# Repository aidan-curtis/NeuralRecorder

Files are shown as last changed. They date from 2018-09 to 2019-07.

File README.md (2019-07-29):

<iframe style="width: 100%" height = "500" src="https://www.youtube.com/embed/SluLUA3ErF0" frameborder="0" allow="accelerometer; autoplay; encrypted-media; gyroscope; picture-in-picture" allowfullscreen></iframe>

## Problem Statement
According to the World Health Organization, up to 50 million people in the world have epilepsy. Of these 50 million, 30% do not respond to medication to keep their seizures under control. These patients are said to have intractable epilepsy, and one of the most effective ways of treating these patients is to record patient EEG data in order to determine the source of the seizures, and then remove the specific part of the brain that is causing the seizures. This process of recording data is invasive and requires implanting electrodes into the brain. These electrodes are wired from inside the brain to a stationary external source that collects the data. The presence of wires causes two main problems: 1) the patients have limited mobility throughout the duration of the data recording and must remain in the hospital for days or even weeks, and 2) the wires are a potential source of infection.

Remaining in the hospital for an extended period of time is extremely expensive, and if the wires were to cause an infection, that cost would only go up. The estimated cost for this procedure is about $10,000 a day. Additionally, being unable to move about unrestricted is detrimental to the patient’s general well-being.

We aim to design a device that can be implanted into a patient’s brain and transmit EEG data wirelessly. Such a device can decrease hospital stay with the possibility of the patient going home for the duration of the recording process, and will drastically decrease the cost of the process. Additionally, even if the patient must remain in the hospital, our device will allow the patient to move about the room freely, which will greatly improve their quality of life. Lastly, our device will also implement novel data compression techniques prior to transmission, which sets our product apart from existing solutions.

## Project Scope
We will build a fully functioning wireless neural recording system that uses data compression to efficiently transmit local field potentials and/or single unit action potential data from patients to a nearby data collection device.

It will contain four major subsystems:
- A power management system
- Frontend interface chip that does signal conditioning
- A wireless link to a receiver
- A novel data compression implementation

With a budget of $2,500 and working between August 29, 2018 and April 11, 2019 we must meet or exceed a minimum set of requirements:
- 48 electrode channels consisting of 6 probes with 8 electrodes each
- A battery life 24 hours or greater
- An ADC resolution of at least 8 bits
- Ability to wirelessly transmit data at least 1 meter
- A Sampling rate of at least 1000 Hz

## Final Design

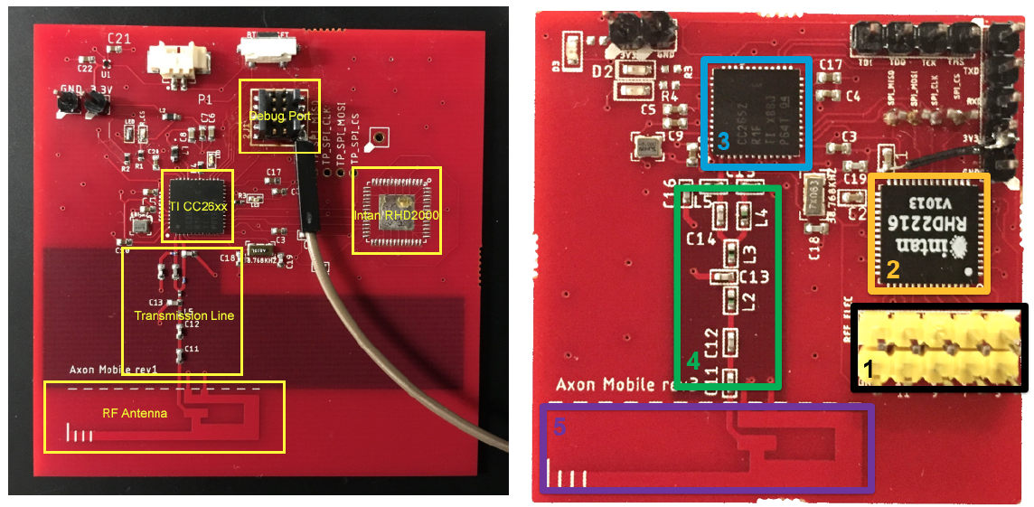
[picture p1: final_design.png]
Final Design


## Intracranial Testing
<iframe style="width: 100%" height = "500" src="https://www.youtube.com/embed/LJeJShj3aGc" frameborder="0" allow="accelerometer; autoplay; encrypted-media; gyroscope; picture-in-picture" allowfullscreen></iframe>

## ISCAS World Champions
We placed first in the ISCAS Compatition in Sapporo, Japan.
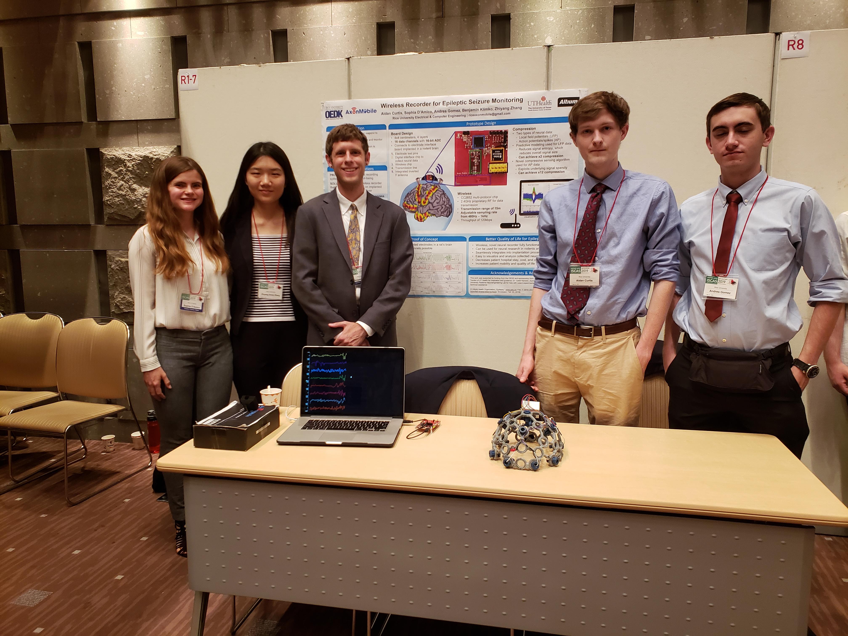
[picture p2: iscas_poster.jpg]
ISCAS Award

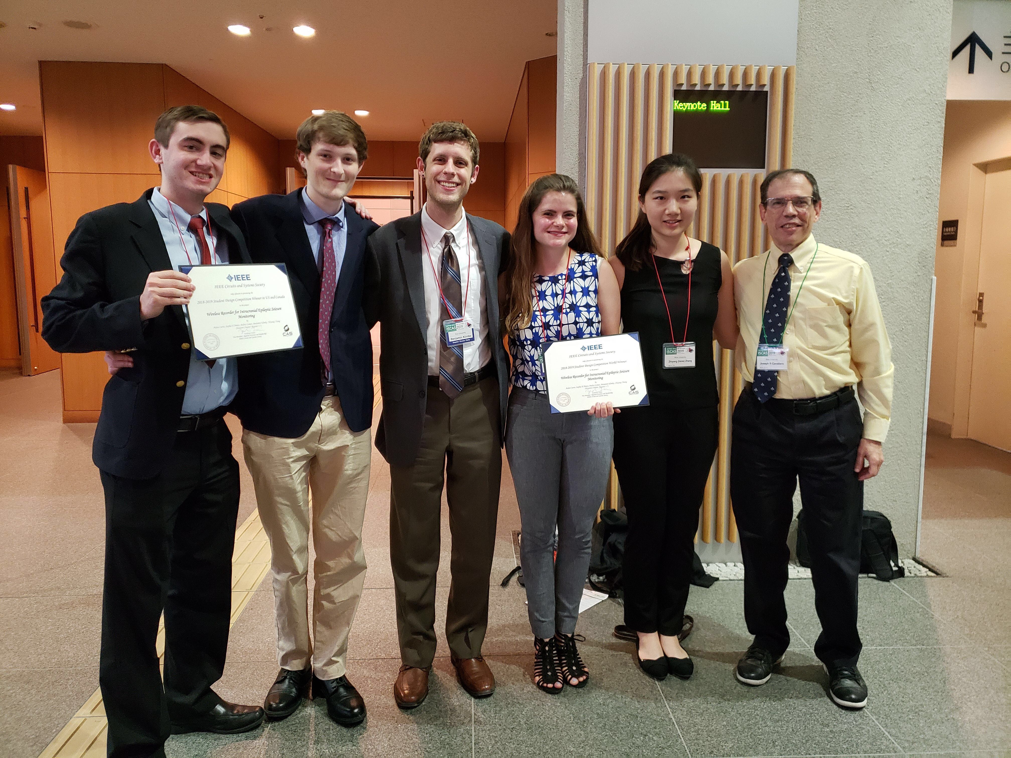
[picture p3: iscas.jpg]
ISCAS Poster


## Full Report
[Download Full Report PDF]( FullReport.pdf )

## Team
Team Axon Mobile
- *Aidan Curtis:* arc11 at rice dot edu
- *Sophie D'Amico:* srd5 at rice dot edu
- *Benjamin Klimko:* bhk2 at rice dot edu
- *Irene Zhang:* zz36 at rice dot edu
- *Andres Gomez:* aeg6 at rice dot edu

## Sponsorship
Thanks to Altium for sponsoring our team and providing us with Altium Designer so we can easily and efficiently create custom PCBs for our project.

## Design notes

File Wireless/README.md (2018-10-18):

### Stream Data From An Arduino
Code to be updated. You need to install Matlab Arduino support first 
https://www.mathworks.com/hardware-support/arduino-matlab.html

### Writing code for TI MCUs
* You can use TI CCS Cloud IDE for development. Go to https://dev.ti.com/ and select CCS Cloud.
* Import Project Empty, run the code and follow instructions to install Chrome 
extension and cloud dependencies. 

### View Throughput
* SmartRF Protocol Packet Sniffer http://www.ti.com/tool/packet-sniffer can be used to 
see the data that are being broadcasted

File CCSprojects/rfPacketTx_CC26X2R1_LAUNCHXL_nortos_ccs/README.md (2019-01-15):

---
# rfpackettx

---

Example Summary
---------------
The Packet TX example illustrates how to do simple packet transmission using
the RF driver. This example is meant to be used with the Packet RX
example or SmartRF Studio. For every packet transmitted, Board_PIN_LED1 is
toggled.  The frequency and other RF settings can be modified using SmartRF
Studio.

Peripherals Exercised
---------------------
* `Board_PIN_LED1` - Toggled when data is transmitted over the RF interface

Resources & Jumper Settings
---------------------------
> If you're using an IDE (such as CCS or IAR), please refer to Board.html in
your project directory for resources used and board-specific jumper settings.
Otherwise, you can find Board.html in the directory
&lt;SDK_INSTALL_DIR&gt;/source/ti/boards/&lt;BOARD&gt;.

Example Usage
-------------
Run the example. On another board, run the Packet RX example.
Board_PIN_LED1 is toggled when data is transmitted.

Application Design Details
--------------------------
This examples consists of a single task and the exported SmartRF Studio radio
settings.

The default frequency is 868.0 MHz. In order to change frequency, modify the
smartrf_settings file. This can be done using the code export feature in
Smart RF Studio, or directly in the file.

The default frequency is 868.0 MHz, in order to change RF settings please
modify the smartrf_settings.c file.
This can be done either by exporting from Smart RF Studio or directly in the
file.

When the task is executed it:

1. Configures the radio for Proprietary mode
2. Gets access to the radio via the RF drivers RF_open
3. Sets up the radio using CMD_PROP_RADIO_DIV_SETUP command
4. Set the output power to 14 dBm (requires that CCFG_FORCE_VDDR_HH = 1 in
ccfg.c)
5. Sets the frequency using CMD_FS command
6. Create packet (with increasing sequence number and random content)
7. Set absolute TX time to utilize automatic power management
8. Transmit packet using CMD_PROP_TX command with blocking RF driver call
9. Toggle Board_PIN_LED1 to indicate packet transmitted
10. Transmit packets forever by repeating step 6-9

Note for IAR users: When using the CC1310DK, the TI XDS110v3 USB Emulator must
be selected. For the CC1310_LAUNCHXL, select TI XDS110 Emulator. In both cases,
select the cJTAG interface.

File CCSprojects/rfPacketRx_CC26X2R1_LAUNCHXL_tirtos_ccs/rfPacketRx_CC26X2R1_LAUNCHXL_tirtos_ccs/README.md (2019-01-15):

---
# rfpacketrx

---

Example Summary
---------------
The Packet RX example illustrates how to do simple packet RX using the
RF driver. This example is meant to be used with the Packet TX example or
SmartRF Studio. For every packet received, Board_PIN_LED2 is toggled.
The frequency and other RF settings can be modified using SmartRF Studio.

Peripherals Exercised
---------------------
* `Board_PIN_LED2` - Toggled when data is received over the RF interface

Resources & Jumper Settings
---------------------------
> If you're using an IDE (such as CCS or IAR), please refer to Board.html in
your project directory for resources used and board-specific jumper settings.
Otherwise, you can find Board.html in the directory
&lt;SDK_INSTALL_DIR&gt;/source/ti/boards/&lt;BOARD&gt;.

Example Usage
-------------
Run the example. On another board, run the EasyLink TX example.
Board_PIN_LED2 is toggled when data with CRC OK is received.

Application Design Details
--------------------------
This examples consists of a single task and the exported SmartRF Studio radio
settings.

The default frequency is 868.0 MHz. In order to change frequency, modify the
smartrf_settings file. This can be done using the code export feature in
Smart RF Studio, or directly in the file.

The default frequency is 868.0 MHz, in order to change RF settings please
modify the smartrf_settings.c file.
This can be done either by exporting from Smart RF Studio or directly in the
file.

When the task is executed it:

1. Configures the radio for Proprietary mode
2. Gets access to the radio via the RF drivers RF_open
3. Sets up the radio using CMD_PROP_RADIO_DIV_SETUP command
4. Defines a data queue to handle received data
5. Sets the frequency using CMD_FS command
6. Sends the CMD_PROP_RX command to start receiving data
7. Once data with CRC OK is received we toggle the
   Board_PIN_LED2 and re-enter RX with the CMD_PROP_RX command

Note for IAR users: When using the CC1310DK, the TI XDS110v3 USB Emulator must
be selected. For the CC1310_LAUNCHXL, select TI XDS110 Emulator. In both cases,
select the cJTAG interface.

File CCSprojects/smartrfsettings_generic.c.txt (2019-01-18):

//*********************************************************************************
// These settings have been generated for use with TI-RTOS and cc26xxware
//
// Generated by SmartRF Studio version 2.3.0
// Tested with TI-RTOS version tirtos_simplelink_2_16_xx_xx
//
//*********************************************************************************

//*********************************************************************************
// Parameter summary
// Address: aa-bb
// Frequency: 2445.00000 MHz
// Data Format: Serial mode disable
// Deviation: 50.000 kHz
// Packet Length Config: Variable
// Max Packet Length: 128
// Packet Length: 30
// RX Filter BW: 220 kHz
// Symbol Rate: 50.00000 kBaud
// Sync Word Length: 32 Bits
// TX Power: 5 dBm
// Whitening: No whitening

#include <ti/devices/DeviceFamily.h>
#include DeviceFamily_constructPath(driverlib/rf_mailbox.h)
#include DeviceFamily_constructPath(driverlib/rf_common_cmd.h)
#include DeviceFamily_constructPath(driverlib/rf_prop_cmd.h)

#include <ti/drivers/rf/RF.h>
#include "smartrf_settings.h"

// TI-RTOS RF Mode Object
RF_Mode RF_prop =
{
    .rfMode = RF_MODE_PROPRIETARY_2_4,
//    .rfMode = RF_MODE_BLE,
    .cpePatchFxn = 0, //&rf_patch_cpe_genfsk,
    .mcePatchFxn = 0, //&rf_patch_mce_genfsk,
    .rfePatchFxn = 0, //&rf_patch_rfe_genfsk,
};

uint32_t shape[] = {0x00000000, 0x00000000, 0x00000000, 0x360c0100, 0xacaba076, 0xacacacac};

// Overrides for CMD_PROP_RADIO_SETUP
uint32_t pOverrides[] = {
 // override_agama_48_mhz_crystal.xml
 // Calculate the frequencies for synth based on 48MHz crystal (default is 24MHz).
 (uint32_t)0x00400403,
 // override_turn_off_dcdc_option.xml
 // Set DCDCCTL5[3:0]=0x0, Turn off optimization of DCDC regulator in TX
 (uint32_t)0x000088D3,
 // Set DCDCCTL5[3:0]=0x0, Turn off optimization of DCDC regulator in RX
 (uint32_t)0x000088C3,
 (uint32_t)0xFFFFFFFF,
};

// CMD_PROP_RADIO_SETUP
rfc_CMD_PROP_RADIO_SETUP_t RF_cmdPropRadioDivSetup =
{
    .commandNo = 0x3806,
    .status = 0x0000,
    .pNextOp = 0, // INSERT APPLICABLE POINTER: (uint8_t*)&xxx
    .startTime = 0x00000000,
    .startTrigger.triggerType = 0x0,
    .startTrigger.bEnaCmd = 0x0,
    .startTrigger.triggerNo = 0x0,
    .startTrigger.pastTrig = 0x0,
    .condition.rule = 0x1,
    .condition.nSkip = 0x0,
    .modulation.modType = 0x1,
    .modulation.deviation = 200,
    .symbolRate.preScale = 15,
    .symbolRate.rateWord = 131072,
    .rxBw = 7,
    .preamConf.nPreamBytes = 0x8,
    .preamConf.preamMode = 0x0,
    .formatConf.nSwBits = 16,
    .formatConf.bBitReversal = 0x0,
    .formatConf.bMsbFirst = 0x1,
    .formatConf.fecMode = 0x0,
    .formatConf.whitenMode = 0x0,
    .config.frontEndMode = 0x0,
    .config.biasMode = 0x0,
    .config.analogCfgMode = 0x0,
    .config.bNoFsPowerUp = 0x0,
    .txPower = 0x9324,
    .pRegOverride = pOverrides,
};

// CMD_FS
rfc_CMD_FS_t RF_cmdFs =
{
    .commandNo = 0x0803,
    .status = 0x0000,
    .pNextOp = 0, // INSERT APPLICABLE POINTER: (uint8_t*)&xxx
    .startTime = 0x00000000,
    .startTrigger.triggerType = 0x0,
    .startTrigger.bEnaCmd = 0x0,
    .startTrigger.triggerNo = 0x0,
    .startTrigger.pastTrig = 0x0,
    .condition.rule = 0x1,
    .condition.nSkip = 0x0,
    .frequency = 2440,
    .fractFreq = 0x0000,
    .synthConf.bTxMode = 1,
    .synthConf.refFreq = 0x0,
};

// CMD_PROP_TX
rfc_CMD_PROP_TX_t RF_cmdPropTx =
{
    .commandNo = 0x3801,
    .status = 0x0000,
    .pNextOp = 0, // INSERT APPLICABLE POINTER: (uint8_t*)&xxx
    .startTime = 0x00000000,
    .startTrigger.triggerType = 0x0,
    .startTrigger.bEnaCmd = 0x0,
    .startTrigger.triggerNo = 0x0,
    .startTrigger.pastTrig = 0x0,
    .condition.rule = 0x1,
    .condition.nSkip = 0x0,
    .pktConf.bFsOff = 0x0,
    .pktConf.bUseCrc = 0x1,
    .pktConf.bVarLen = 0x1,
    .pktLen = 0x7d, // SET APPLICATION PAYLOAD LENGTH
    .syncWord = 0xD391D391,
    .pPkt = 0, // INSERT APPLICABLE POINTER: (uint8_t*)&xxx
};

// CMD_PROP_RX
rfc_CMD_PROP_RX_t RF_cmdPropRx =
{
    .commandNo = 0x3802,
    .status = 0x0000,
    .pNextOp = 0, // INSERT APPLICABLE POINTER: (uint8_t*)&xxx
    .startTime = 0x00000000,
    .startTrigger.triggerType = 0x0,
    .startTrigger.bEnaCmd = 0x0,
    .startTrigger.triggerNo = 0x0,
    .startTrigger.pastTrig = 0x0,
    .condition.rule = 0x1,
    .condition.nSkip = 0x0,
    .pktConf.bFsOff = 0x0,
    .pktConf.bRepeatOk = 0x0,
    .pktConf.bRepeatNok = 0x0,
    .pktConf.bUseCrc = 0x1,
    .pktConf.bVarLen = 0x1,
    .pktConf.bChkAddress = 0x0,
    .pktConf.endType = 0x0,
    .pktConf.filterOp = 0x0,
    .rxConf.bAutoFlushIgnored = 0x0,
    .rxConf.bAutoFlushCrcErr = 0x0,
    .rxConf.bIncludeHdr = 0x1,
    .rxConf.bIncludeCrc = 0x0,
    .rxConf.bAppendRssi = 0x0,
    .rxConf.bAppendTimestamp = 0x0,
    .rxConf.bAppendStatus = 0x1,
    .syncWord = 0xD391D391,
    .maxPktLen = 0x7d, // MAKE SURE DATA ENTRY IS LARGE ENOUGH
//    .pktConf.addressMode = 0, // CHANGE!
    .address0 = 0xaa,
    .address1 = 0xbb,
    .endTrigger.triggerType = 0x1,
    .endTrigger.bEnaCmd = 0x0,
    .endTrigger.triggerNo = 0x0,
    .endTrigger.pastTrig = 0x0,
    .endTime = 0x00000000,
    .pQueue = 0, // INSERT APPLICABLE POINTER: (dataQueue_t*)&xxx
    .pOutput = 0, // INSERT APPLICABLE POINTER: (uint8_t*)&xxx
};

// CMD_TX_TEST
rfc_CMD_TX_TEST_t RF_cmdTxTest =
{
        .commandNo = 0x0808,
        .status = 0x0000,
        .pNextOp = 0, /*INSERT APPLICABLE POINTER: (uint8_t*)&xxx */
        .startTime = 0x00000000,
        .startTrigger.triggerType = 0x0,
        .startTrigger.bEnaCmd = 0x0,
        .startTrigger.triggerNo = 0x0,
        .startTrigger.pastTrig = 0x0,
        .condition.rule = 0x1,
        .condition.nSkip = 0x0,
        .config.bUseCw = 0x0,
        .config.bFsOff = 0x0,
        .config.whitenMode = 0x2,
        .__dummy0 = 0x00,
        .txWord = 0xabcd,
        .__dummy1 = 0x00,
        .endTrigger.triggerType = 0x1,
        .endTrigger.bEnaCmd = 0x0,
        .endTrigger.triggerNo = 0x0,
        .endTrigger.pastTrig = 0x0,
        .syncWord = 0x930b51de,
        .endTime = 0x00000000,
};

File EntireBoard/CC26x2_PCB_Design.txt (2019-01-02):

CC26x2 Doc List
=======================
General
CC26xx Tools Overview
	- http://processors.wiki.ti.com/index.php/CC13xx_CC26xx_Tools_Overview#Using_CCS_v6.1_with_XDS110_and_CC13xx.2FCC26xx
CC2652R1 Quick Start Guide
	- http://www.ti.com/lit/ml/swru528/swru528.pdf
CC26x0 SimpleLink Wireless MCU Technical Reference Guide
	- http://www.ti.com/lit/ug/swcu185a/swcu185a.pdf
Production Test and Programming for CC26xx
	- http://processors.wiki.ti.com/index.php/Production_Test_and_Programming_of_SimpleLink_CC26xx_or_CC13xx_Wireless_MCUs
Design a product with CC26xx
	- http://processors.wiki.ti.com/index.php/Designing_a_Product_with_SimpleLink_CC26xx_or_CC13xx_Wireless_MCUs#Step_6_-_Test_the_hardware
	- Very useful links
-----------------------
PCB Design
CC26xx Hardware Layout Considerations
	- http://processors.wiki.ti.com/images/8/8b/CC26xx_HW_training_Layout_Considerations.pdf
CC26xx RF Frontends and Antennas
	- http://processors.wiki.ti.com/images/4/45/CC26xx_HW_training_RF_Frontends_and_Antennas.pdf
	- Differential vs Single-ended design. Differential vs Balun. External vs Internal bias
2.4GHz Inverted F Antenna
	- http://www.ti.com/lit/an/swru120c/swru120c.pdf
	- GND plane placement wrt antenna
PCB Design Considerations 
	- http://www.ti.com/lit/an/swra640/swra640.pdf 
Johnson Balun for CC26xx Family
	- http://www.ti.com/lit/an/swra572/swra572.pdf 
	- 9 discrete LC components into a single components(basically replacing LC on RF_N and RF_P pins)
	- Complex impedance matching
Hardware Migration from CC26x0 to CC26x2
	- http://www.ti.com/lit/an/swra582/swra582.pdf
Crystal Selection
	- http://processors.wiki.ti.com/index.php/CC26xx_Crystals
XDS110 Debug Probe guide
	- http://www.ti.com/lit/ug/sprui94/sprui94.pdf	
CC Debugger User Guide 
	- http://www.ti.com/lit/ug/swru197h/swru197h.pdf
-----------------------
Software
CC26xx Family SW Quick Start Guide
	- http://processors.wiki.ti.com/index.php/CC26xx_Family_SW_Quickstart_Guide
Flash Programming via JTAG Port
	- https://e2e.ti.com/support/wireless-connectivity/bluetooth/f/538/p/556076/2033879?tisearch=e2e-sitesearch&keymatch=%20user%3A290509#2033879
CC26xx JTAG Flash Programming
	- https://e2e.ti.com/support/wireless-connectivity/bluetooth/f/538/t/521220
SmartRF Flash Programmer User Manual
	- http://www.ti.com/lit/ug/swru069g/swru069g.pdf
	- NOTE that CC26x2 is not supported
CCS Uniflash
	- http://processors.wiki.ti.com/index.php/Category:CCS_UniFlash
Uniflash v4 Quick Guide
	- http://processors.wiki.ti.com/index.php/UniFlash_v4_Quick_Guide
JTAG and Uniflash Video Tutorial
	- https://training.ti.com/using-jtag-ucd3138-introduction-uniflash

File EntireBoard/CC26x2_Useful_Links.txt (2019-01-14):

CC26x2 Doc List
=======================
General
CC2652R Datasheet
	- http://www.ti.com/lit/ds/symlink/cc2652r.pdf
CC26xx Tools Overview
	- http://processors.wiki.ti.com/index.php/CC13xx_CC26xx_Tools_Overview#Using_CCS_v6.1_with_XDS110_and_CC13xx.2FCC26xx
CC2652R1 Quick Start Guide
	- http://www.ti.com/lit/ml/swru528/swru528.pdf
CC26x0 SimpleLink Wireless MCU Technical Reference Guide
	- http://www.ti.com/lit/ug/swcu185a/swcu185a.pdf
Production Test and Programming for CC26xx
	- http://processors.wiki.ti.com/index.php/Production_Test_and_Programming_of_SimpleLink_CC26xx_or_CC13xx_Wireless_MCUs
Design a product with CC26xx
	- http://processors.wiki.ti.com/index.php/Designing_a_Product_with_SimpleLink_CC26xx_or_CC13xx_Wireless_MCUs#Step_6_-_Test_the_hardware
	- Very useful links
-----------------------
PCB Design
CC26xx Hardware Design Checklist
	- http://processors.wiki.ti.com/index.php/CC26xx_HW_Checklist
CC26xx Hardware Layout Considerations
	- http://processors.wiki.ti.com/images/8/8b/CC26xx_HW_training_Layout_Considerations.pdf
CC26xx RF Frontends and Antennas
	- http://processors.wiki.ti.com/images/4/45/CC26xx_HW_training_RF_Frontends_and_Antennas.pdf
	- Differential vs Single-ended design. Differential vs Balun. External vs Internal bias
2.4GHz Inverted F Antenna
	- http://www.ti.com/lit/an/swru120c/swru120c.pdf
	- GND plane placement wrt antenna
CC26xx PCB Design Considerations 
	- http://www.ti.com/lit/an/swra640/swra640.pdf 
Johanson Balun for CC26xx Family
	- http://www.ti.com/lit/an/swra572/swra572.pdf 
	- 9 discrete LC components into a single components(basically replacing LC on RF_N and RF_P pins)
	- Complex impedance matching
Hardware Migration from CC26x0 to CC26x2
	- http://www.ti.com/lit/an/swra582/swra582.pdf
Crystal Selection
	- http://processors.wiki.ti.com/index.php/CC26xx_Crystals
XDS110 Debug Probe guide
	- http://www.ti.com/lit/ug/sprui94/sprui94.pdf	
CC Debugger User Guide 
	- http://www.ti.com/lit/ug/swru197h/swru197h.pdf
-----------------------
Software
CC26xx Family SW Quick Start Guide
	- http://processors.wiki.ti.com/index.php/CC26xx_Family_SW_Quickstart_Guide
Flash Programming via JTAG Port
	- https://e2e.ti.com/support/wireless-connectivity/bluetooth/f/538/p/556076/2033879?tisearch=e2e-sitesearch&keymatch=%20user%3A290509#2033879
CC26xx JTAG Flash Programming
	- https://e2e.ti.com/support/wireless-connectivity/bluetooth/f/538/t/521220
SmartRF Flash Programmer User Manual
	- http://www.ti.com/lit/ug/swru069g/swru069g.pdf
	- NOTE that CC26x2 is not supported
CCS Uniflash
	- http://processors.wiki.ti.com/index.php/Category:CCS_UniFlash
Uniflash v4 Quick Guide
	- http://processors.wiki.ti.com/index.php/UniFlash_v4_Quick_Guide
JTAG and Uniflash Video Tutorial
	- https://training.ti.com/using-jtag-ucd3138-introduction-uniflash

-----------------------
Bluetooth
TI Serial Port Service
	- http://www.ti.com/lit/ug/tidua63/tidua63.pdf

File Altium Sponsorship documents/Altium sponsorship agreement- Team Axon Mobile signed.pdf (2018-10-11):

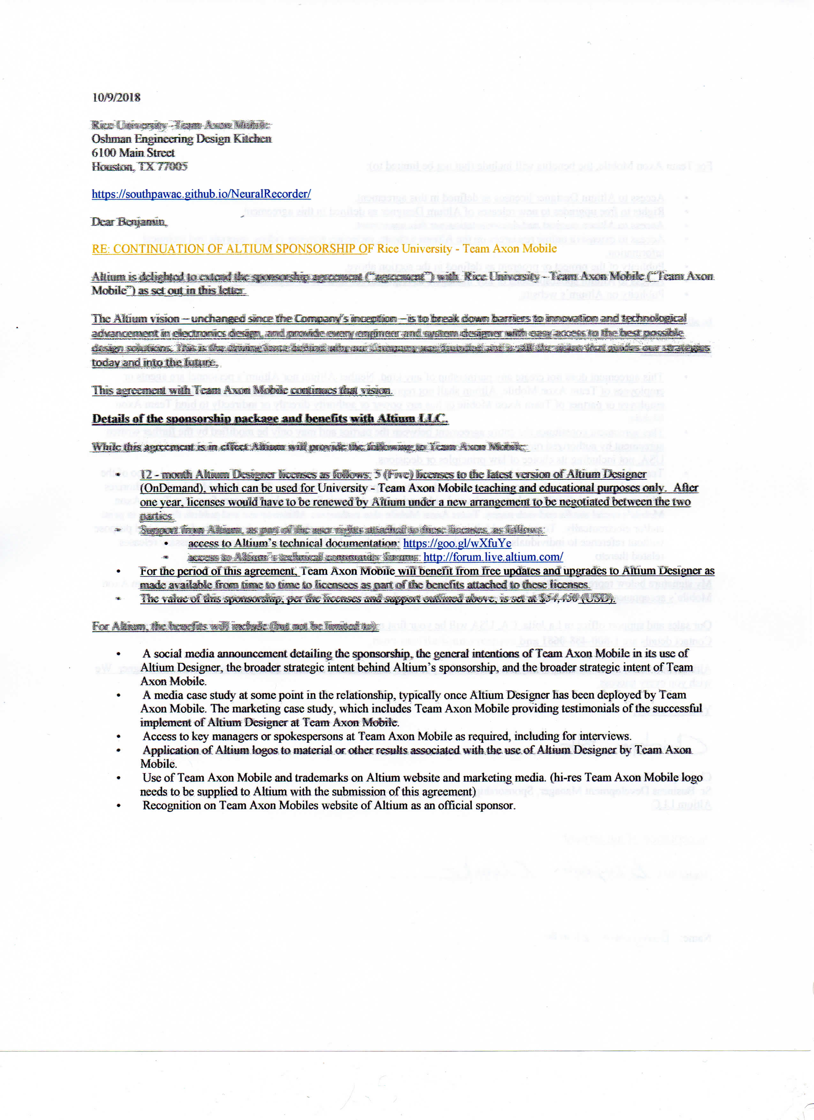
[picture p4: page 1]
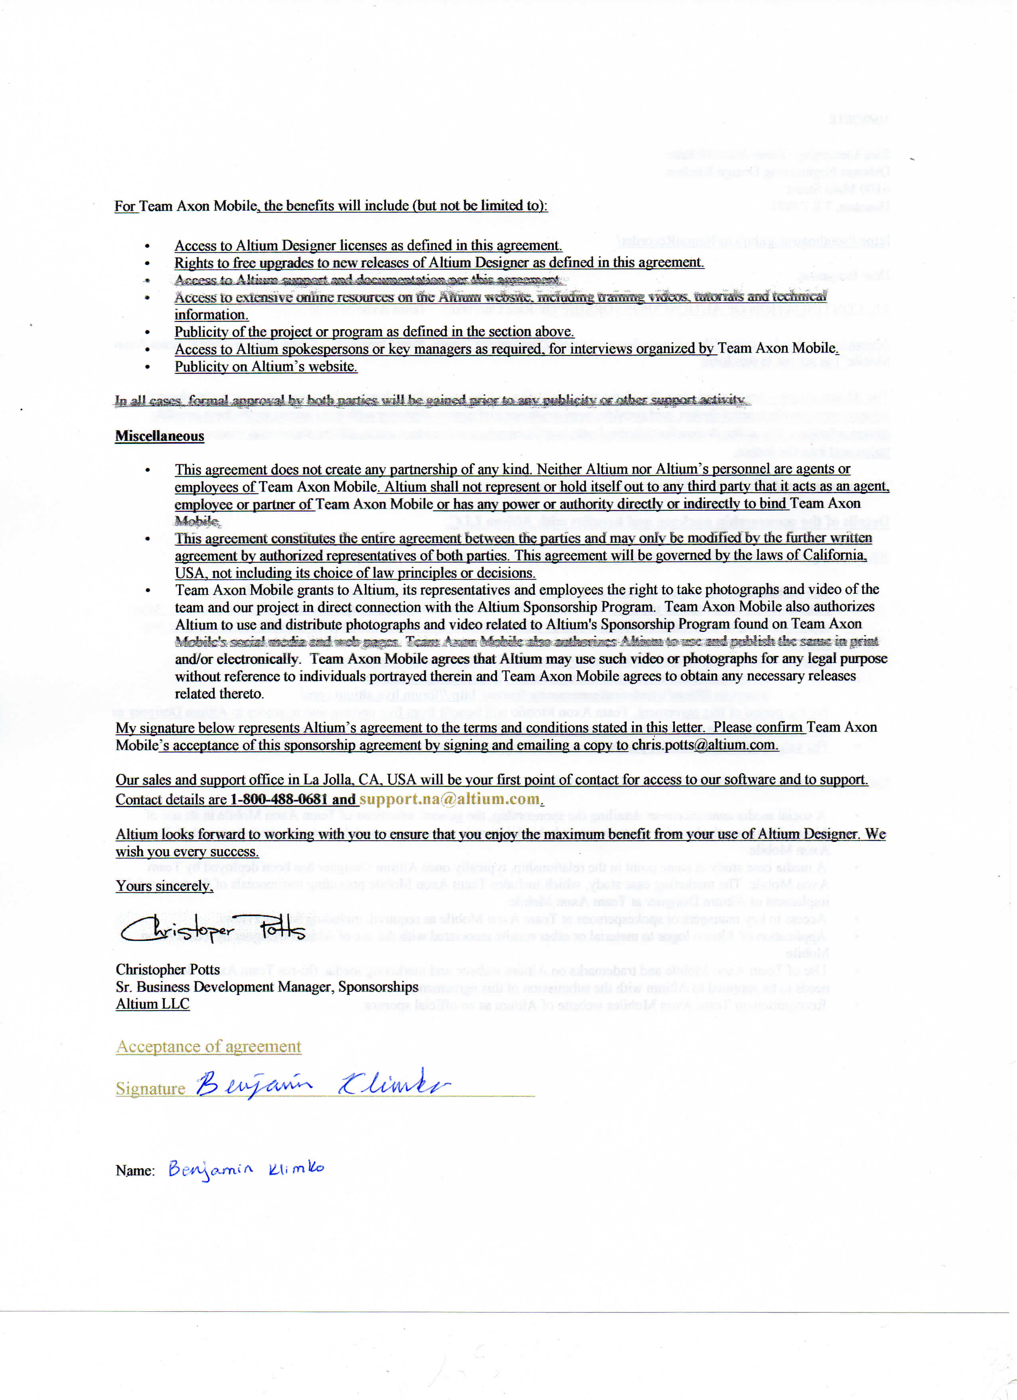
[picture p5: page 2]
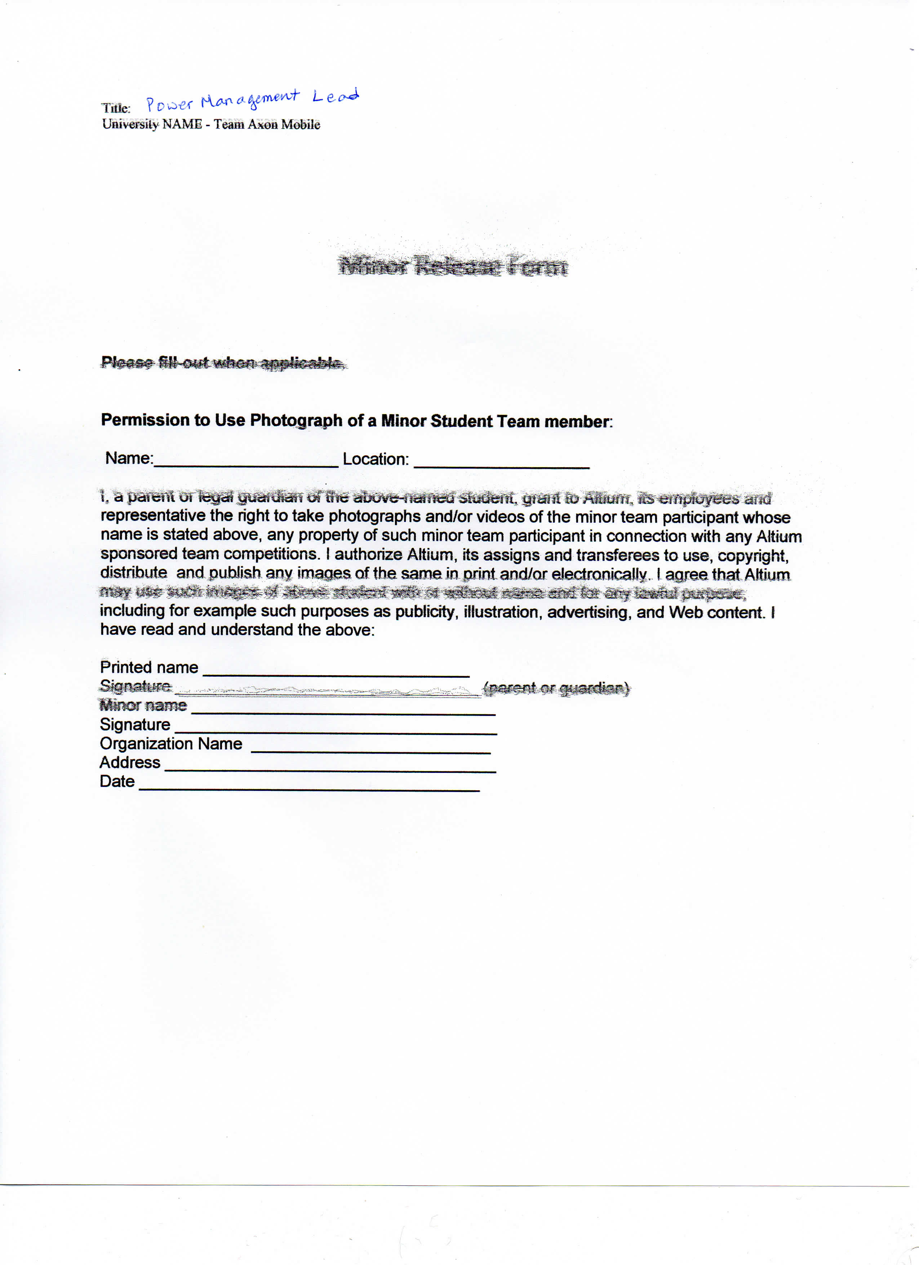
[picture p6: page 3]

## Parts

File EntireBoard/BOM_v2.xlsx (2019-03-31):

Name | Description | MPN | Supplier Name | Supplier Part # | Unit Price | Quantity | Total Price | Link | Datasheet
48MHz Crystal | required as frequency reference for radio | NDK NX2016SA 48.000MHz EXS00A-CS05517 | Digikey | 644-1377-1-ND | $0.86 | 3 | $2.58 | https://www.digikey.com/product-detail/en/ndk-america-inc/NX2016SA-48MHZ-EXS00A-CS05517/644-1377-1-ND/9172105 | https://media.digikey.com/pdf/Data%20Sheets/NDK%20PDFs/NX2016SA-48M-EXS00A-CS05517_Spec.pdf
32.768kH Crystal | reduce power consumption for BLE compared to internal RC oscillator | Epson FC-135 | Digikey | SE2413CT-ND | 0.41 | 3 | $1.23 | https://www.digikey.com/product-detail/en/epson/FC-135-32.7680KA-A3/SE2413CT-ND/569857 | https://support.epson.biz/td/api/doc_check.php?dl=brief_FC-135&lang=en
10pin microheader | connection to XDS110 debugger | FTSH-105-01-F-DV-K-TR | Digikey | SAM13160CT-ND | 3.36 | 3 | $10.08 | https://www.digikey.com/product-detail/en/samtec-inc/FTSH-105-01-F-DV-K-TR/SAM13160CT-ND/8827915 | http://suddendocs.samtec.com/catalog_english/ftsh_smt.pdf
IDC ribbon cable | connection btw XDS110 and CC | Samtek FFSD-05-D-02.00-01-N | Digikey | SAM8217-ND | 7.86 | 1 | $7.86 | https://www.digikey.com/product-detail/en/samtec-inc/FFSD-05-D-02.00-01-N/SAM8217-ND/1106576 | http://suddendocs.samtec.com/catalog_english/ffsd.pdf
current sense resistor | measure power consumption | Panasonic ERJ-MFBAF10MX | Mouser | 667-ERJ-MFBAF10MX | $0.61 | 4 | $2.44 | https://www.mouser.com/ProductDetail/Panasonic/ERJ-MFBAF10MX | https://www.mouser.com/datasheet/2/315/RDN0000C328-1365505.pdf
green led | signal line indication | Bivar SM0402GC | Mouser | 749-SM0402GC | $0.57 | 12 | $6.84 | https://www.mouser.com/ProductDetail/Bivar/SM0402GC | https://www.mouser.com/datasheet/2/50/Bivar-3-22-2017-SM0402GC-1158932.pdf
switch | for resetting mcu | 1188E-1K2-V-T/R | Mouser | 113-1188E1K2VTR | $0.69 | 3 | $2.07 | https://www.mouser.com/ProductDetail/Diptronics/1188E-1K2-V-T-R?qs=MLItCLRbWswadUUxegNFmg%3D%3D | http://www.dip.com.tw/en/en-product-information/en-switch004/item/2445-1188
batteries | powering system | RJD3555HPPV30M | Digikey | 1572-1627-ND | $34.13 | 2 | $68.26 | https://www.digikey.com/product-detail/en/illinois-capacitor/RJD3555HPPV30M/1572-1627-ND/6159145
battery connector | connect the power to the system | 532610271 | Digikey | WM7620CT-ND | $0.98 | 4 | $3.92
1.5 kOhm Ferrite Bead | Part of the power system from cc2650 | BLM18HE152SN1D | Digikey | 490-5216-1-ND | $0.21 | 3 | $0.63 | https://www.digikey.com/product-detail/en/murata-electronics-north-america/BLM18HE152SN1D/490-5216-1-ND/1948392
22uF cap |  | CL05A226MQ5N6J8 | Digikey | 1276-7090-1-ND | $0.58 | 6 | $3.48 | https://www.digikey.com/product-detail/en/samsung-electro-mechanics/CL05A226MQ5N6J8/1276-7090-1-ND/7320732
1.8pF cap |  | 500R07S1R8BV4T | Digikey | 712-1271-1-ND | $0.21 | 3 | $0.63 | https://www.digikey.com/product-detail/en/johanson-technology-inc/500R07S1R8BV4T/712-1271-1-ND/1786733
12pF cap |  | C0402C120J5GACTU | Digikey | 399-1013-1-ND | $0.10 | 12 | $1.20 | https://www.digikey.com/product-detail/en/kemet/C0402C120J5GACTU/399-1013-1-ND/411288
1pF cap |  | 500R07S1R0BV4T | Digikey | 712-1266-1-ND | $0.21 | 9 | $1.89 | https://www.digikey.com/product-detail/en/johanson-technology-inc/500R07S1R0BV4T/712-1266-1-ND/1786728
6.8 uH inductor |  | AIML-0603-6R8K-T | Digikey | 535-11606-1-ND | $0.10 | 3 | $0.30 | https://www.digikey.com/product-detail/en/abracon-llc/AIML-0603-6R8K-T/535-11606-1-ND/2782848
2nH inductor |  | MHQ0603P2N0BTD25 | Mouser | 810-MHQ0603P2N0BTD25 | $0.60 | 6 | $3.60 | https://www.mouser.com/ProductDetail/TDK/MHQ0603P2N0BTD25
2.4nH inductor |  | LQP03TN2N4B02D | Digikey | 490-6724-1-ND | $0.10 | 6 | $0.60 | https://www.digikey.com/product-detail/en/murata-electronics-north-america/LQP03TN2N4B02D/490-6724-1-ND/5802372
 |  |  |  |  |  |  | $117.61

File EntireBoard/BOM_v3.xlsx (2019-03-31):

Name | Description | Manufacturer | MPN | Supplier Name | Supplier Part # | Unit Price | Quantity | Total Price | Link
48MHz Crystal | required as frequency reference for radio | NDK | NX2016SA 48.000MHz EXS00A-CS05517 | Digikey | 644-1377-1-ND | $0.86 | 5 | $4.30 | https://www.digikey.com/product-detail/en/ndk-america-inc/NX2016SA-48MHZ-EXS00A-CS05517/644-1377-1-ND/9172105
32.768kH Crystal | reduce power consumption for BLE compared to internal RC oscillator | Epson | FC-135 | Digikey | SE2413CT-ND | 0.41 | 5 | $2.05 | https://www.digikey.com/product-detail/en/epson/FC-135-32.7680KA-A3/SE2413CT-ND/569857
solderpaste |  | chipquik | SMD291SNL | mouser | 910-SMD291SNL | $15.29 | 0 | $0.00 | https://www.mouser.com/ProductDetail/Chip-Quik/SMD291SNL
10pin microheader | connection to XDS110 debugger | samtek | FTSH-105-01-F-DV-K-TR | Digikey | SAM13160CT-ND | 3.36 | 3 | $10.08 | https://www.digikey.com/product-detail/en/samtec-inc/FTSH-105-01-F-DV-K-TR/SAM13160CT-ND/8827915
IDC ribbon cable | connection btw XDS110 and CC | samtek | FFSD-05-D-02.00-01-N | Digikey | SAM8217-ND | 7.86 | 0 | $0.00 | https://www.digikey.com/product-detail/en/samtec-inc/FFSD-05-D-02.00-01-N/SAM8217-ND/1106576
current sense resistor | measure power consumption | Panasonic | ERJ-MFBAF10MX | Mouser | 667-ERJ-MFBAF10MX | $0.61 | 5 | $3.05 | https://www.mouser.com/ProductDetail/Panasonic/ERJ-MFBAF10MX
red led | indicator light 0603 | osram | LS L296-P2Q2-1 | mouser | 720-LSL296-P2Q2-1-Z | 0.52 | 5 | $2.60 | https://www.mouser.com/ProductDetail/OSRAM-Opto-Semiconductors/LS-L296-P2Q2-1
green led | signal line indication 0603 | osram | LP L296-J2L2-25 | Mouser | 720-LPL296J2L225Z | 0.57 | 5 | $2.85 | https://www.mouser.com/ProductDetail/OSRAM-Opto-Semiconductors/LP-L296-J2L2-25
button | for resetting mcu |  | 1188E-1K2-V-T/R | Mouser | 113-1188E1K2VTR | $0.69 | 0 | $0.00 | https://www.mouser.com/ProductDetail/Diptronics/1188E-1K2-V-T-R?qs=MLItCLRbWswadUUxegNFmg%3D%3D
switch | power on | E-switch | EG1271 | mouser | 612-EG1271 | $0.76 | 5 | $3.80 | https://www.mouser.com/ProductDetail/E-Switch/EG1271
batteries | powering system |  | RJD3555HPPV30M | Digikey | 1572-1627-ND | $34.13 | 0 | $0.00 | https://www.digikey.com/product-detail/en/illinois-capacitor/RJD3555HPPV30M/1572-1627-ND/6159145
battery connector | connect the power to the system |  | 532610271 | Digikey | WM7620CT-ND | $0.98 | 5 | $4.90 | https://www.digikey.com/product-detail/en/molex/0532610271/WM7620CT-ND/699107
1.5 kOhm Ferrite Bead | Part of the power system from cc2650 |  | BLM18HE152SN1D | Digikey | 490-5216-1-ND | $0.21 | 5 | $1.05 | https://www.digikey.com/product-detail/en/murata-electronics-north-america/BLM18HE152SN1D/490-5216-1-ND/1948392
22uF cap | match TI 0603 | murata | GRM188R60J226MEA0D | mouser | 81-GRM188R60J226ME0D | $0.20 | 10 | $1.95 | https://www.mouser.com/ProductDetail/Murata-Electronics/GRM188R60J226MEA0D?qs=sGAEpiMZZMs0AnBnWHyRQE145Nb6Pjkyo3rf03lmerU%3D
1.8pF cap | match TI 0402 | murata | GRM1555C1H1R8CA01D | mouser | 81-GRM1555C1H1R8CA1D | $0.04 | 10 | $0.40 | https://www.mouser.com/ProductDetail/Murata-Electronics/GRM1555C1H1R8CA01D?qs=sGAEpiMZZMs0AnBnWHyRQJFx1SN4r7R8jjRyTSAQsik%3D
12pF cap | match TI 0402 | murata | GRM1555C1H120JA01D | mouser | 81-GRM1555C1H120JA1D | $0.04 | 20 | $0.80 | https://www.mouser.com/ProductDetail/Murata-Electronics/GRM1555C1H120JA01D?qs=sGAEpiMZZMs0AnBnWHyRQJFx1SN4r7R8pM7YbelYqII%3D
1pF cap | match TI 0402 | murata | GRM1555C1H1R0CA01D | mouser | 81-GRM1555C1H1R0CA1D | $0.04 | 15 | $0.66 | https://www.mouser.com/ProductDetail/Murata-Electronics/GRM1555C1H1R0CA01D
0.1uF cap | match TI | murata | GRM155R71E104KE14D | mouser | 81-GRM155R71E104KE4D | $0.10 | 0 | $0.00
6.8 uH inductor | match TI 0805 | tdk | MLZ2012N6R8LT000 | mouser | 810-MLZ2012N6R8LT000 | $0.14 | 5 | $0.70 | https://www.mouser.com/ProductDetail/TDK/MLZ2012N6R8LT000
6.8uH inductor | 603 | TDK | MLF1608E6R8JT000 | mouser | 810-MLF1608E6R8JT000 | $0.14 | 5 | $0.70 | https://www.mouser.com/ProductDetail/TDK/MLF1608E6R8JT000
2nH inductor 0402 | match TI 0402 | murata | LQG15HS2N0S02D | Mouser | 81-LQG15HS2N0S02D | $0.06 | 10 | $0.56 | https://www.mouser.com/ProductDetail/Murata-Electronics/LQG15HS2N0S02D
2.4nH inductor | match TI 0402 | murata | LQG15HS2N4S02D | mouser | 81-LQG15HS2N4S02D | $0.06 | 10 | $0.60 | https://www.mouser.com/ProductDetail/Murata-Electronics/LQG15HS2N4S02D
intan chip!!!
cc2652 |  |  |  |  |  |  |  | $41.05
linear regulator

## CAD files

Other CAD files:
CCSprojects/ble5_project_zero_cc26x2r1lp_app/FlashROM_Debug/Startup/main.obj
CCSprojects/ble5_project_zero_cc26x2r1lp_app/TOOLS/src/sysbios/m3_Hwi_asm.obj
CCSprojects/rfPacketRx_CC26X2R1_LAUNCHXL_tirtos_ccs/tirtos_builds_CC26X2R1_LAUNCHXL_release_ccs/src/sysbios/m3_IntrinsicsSupport_asm.obj
CCSprojects/rfPacketTx_CC26X2R1_LAUNCHXL_tirtos_ccs/tirtos_builds_CC26X2R1_LAUNCHXL_release_ccs/src/sysbios/m3_Hwi_asm.obj
CCSprojects/ble5_project_zero_cc26x2r1lp_app/TOOLS/src/sysbios/m3_IntrinsicsSupport_asm.obj
CCSprojects/rfPacketRx_CC26X2R1_LAUNCHXL_tirtos_ccs/tirtos_builds_CC26X2R1_LAUNCHXL_release_ccs/src/sysbios/m3_Hwi_asm_switch.obj
CCSprojects/rfPacketTx_CC26X2R1_LAUNCHXL_tirtos_ccs/tirtos_builds_CC26X2R1_LAUNCHXL_release_ccs/src/sysbios/m3_TaskSupport_asm.obj
CCSprojects/ble5_project_zero_cc26x2r1lp_app/TOOLS/src/sysbios/m3_Hwi_asm_switch.obj
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

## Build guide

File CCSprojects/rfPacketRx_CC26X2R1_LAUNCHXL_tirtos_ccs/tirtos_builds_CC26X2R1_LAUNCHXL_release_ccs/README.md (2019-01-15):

## Project Summary

This project contains settings to disable the standard debug features in
TI-RTOS.

## Project Usage

This project is intended to be used by applications that need a "production"
TI-RTOS configuration that does not include debug features.  Multiple
applications can use this project.

This project is the default configuration used by most of the SimpleLink
examples. It was selected as the default to minimize code size.

Please refer to the TI-RTOS Kernel section in the SimpleLink MCU SDK User's
Guide for the details on how applications use this project.

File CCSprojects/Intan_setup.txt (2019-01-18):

   //set up the registers
    messages[0] = 0b0000000000000000;
    messages[1] = 0b0000000000000000;
    messages[2] = 0b1000000011011110; //R0
    messages[3] = 0b1000000100100000; //R1
    messages[4] = 0b1000001000101000; //R2
    messages[5] = 0b1000001100000000; //R3
    messages[6] = 0b1000010011001101; //R4
    messages[7] = 0b1000010100000000; //R5
    messages[8] = 0b1000011000000000; //R6
    messages[9] = 0b1000011100000000; //R7
    messages[10] = 0b1000100000001000; //R8
    messages[11] = 0b1000100100000000; //R9
    messages[12] = 0b1000101000000100; //R10
    messages[13] = 0b1000101100000000; //R11
    messages[14] = 0b1000110000010000; //R12
    messages[15] = 0b1000110101111100; //R13
    messages[16] = 0b1000111011111111; //R14
    messages[17] = 0b1000111111111111; //R15
    messages[18] = 0b1001000011111111; //R16
    messages[19] = 0b1001000111111111; //R17
    messages[20] = 0b0000000000000000;
    messages[21] = 0b0000000000000000;
    messages[22] = 0b0000000000000000;
    messages[23] = 0b0000000000000000;
    messages[24] = 0b0101010100000000; // Config
    messages[25] = 0b0000000000000000;
    messages[26] = 0b0000000000000000;
    messages[27] = 0b0000000000000000;
    messages[28] = 0b0000000000000000;
    messages[29] = 0b0000000000000000;
    messages[30] = 0b0000000000000000;
    messages[31] = 0b0000000000000000;
    messages[32] = 0b0000000000000000;
    messages[33] = 0b0000000000000000;
    messages[34] = 0b0000000000000000;
    messages[35] = 0b0000000000000000;
    messages[36] = 0b1110100000000000; //I
    messages[37] = 0b1110100100000000; //N
    messages[38] = 0b1110101000000000; //T
    messages[39] = 0b1110101100000000; //A
    messages[40] = 0b1110110000000000; //N

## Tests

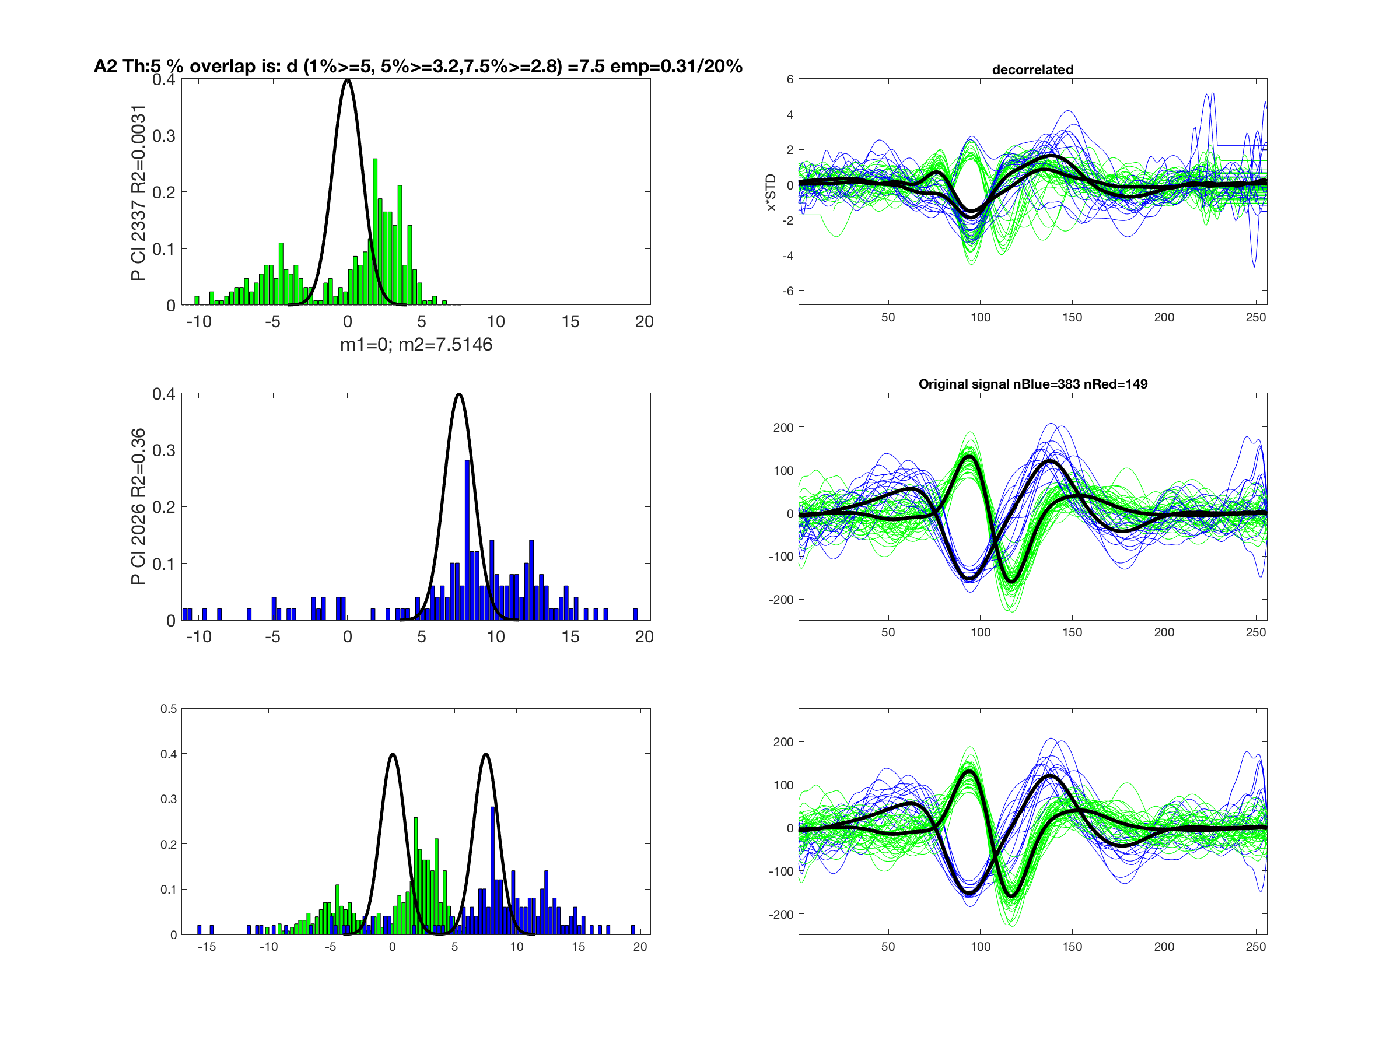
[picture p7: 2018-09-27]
Compression/Mess/5/A2_SepTest_2337_2026_THM_1.png

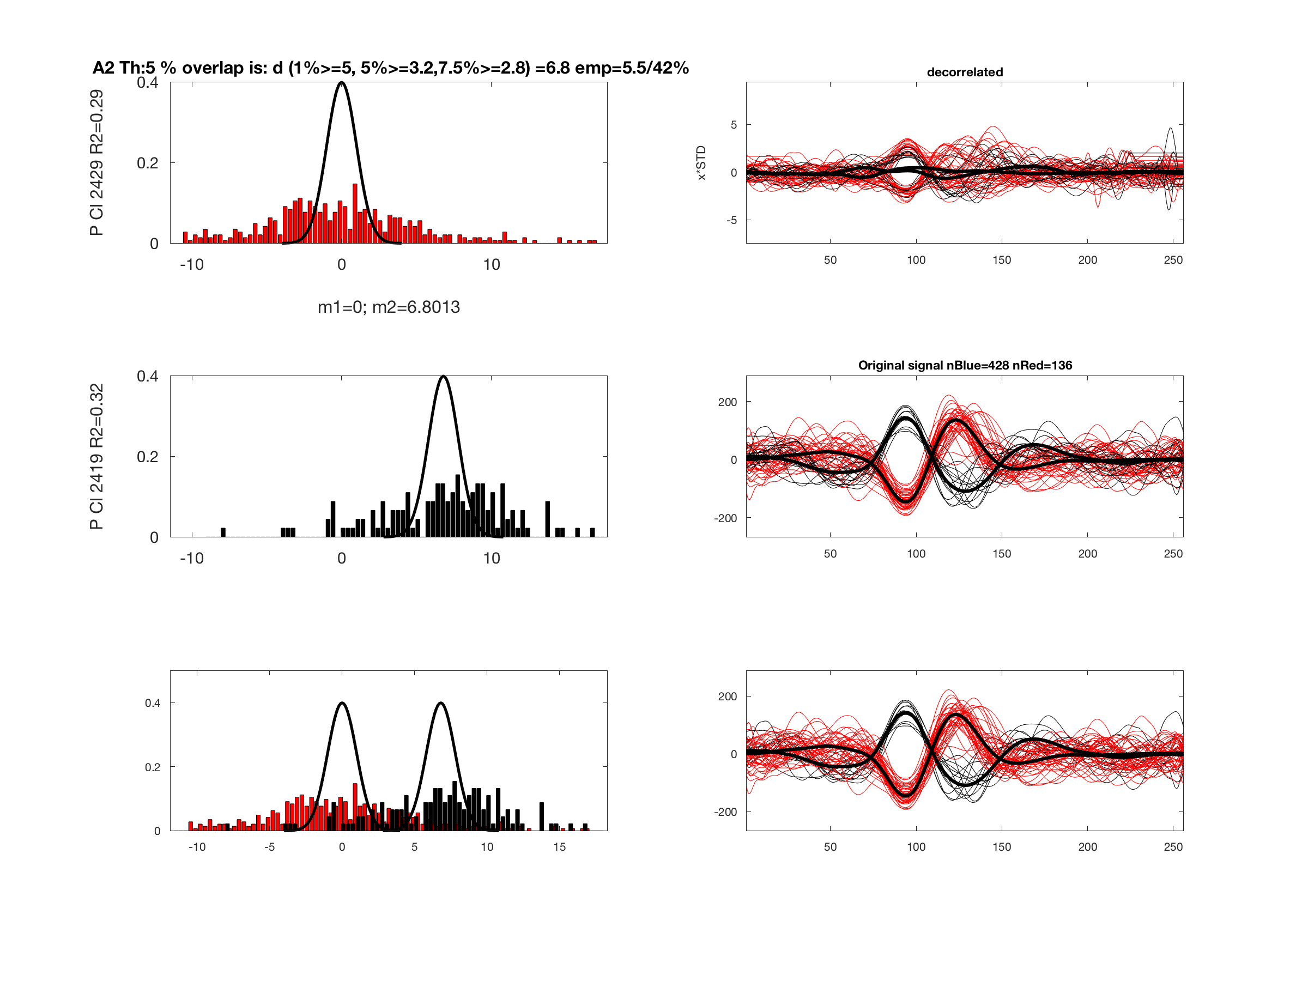
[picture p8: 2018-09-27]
Compression/Mess/5/A2_SepTest_2429_2419_THM_1.png

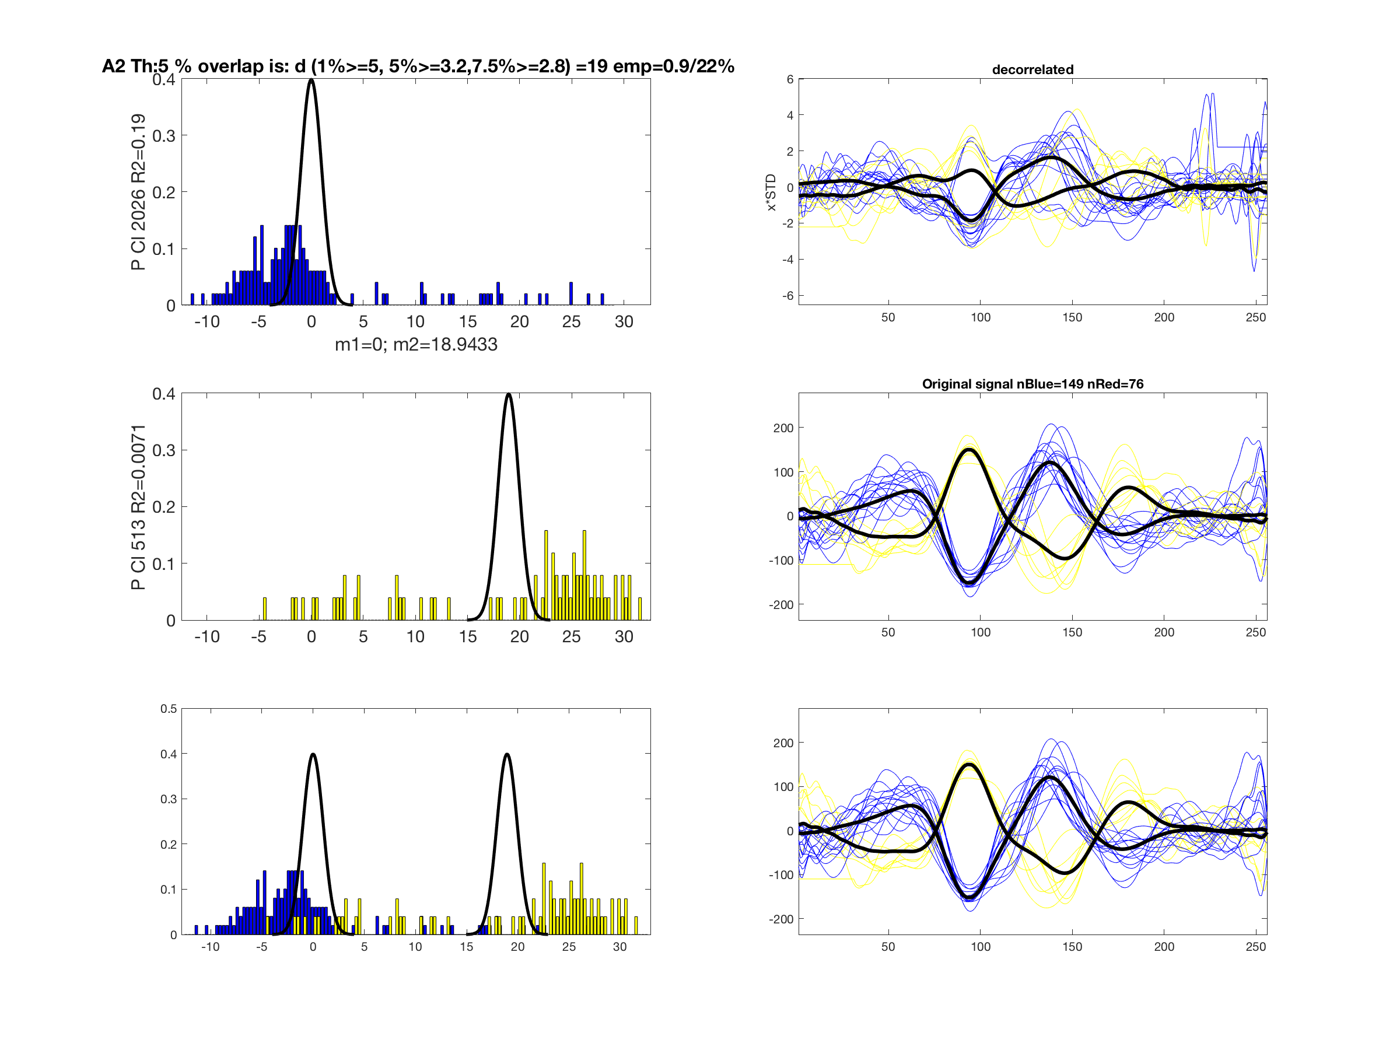
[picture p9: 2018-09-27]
Compression/Mess/5/A2_SepTest_2026_513_THM_1.png

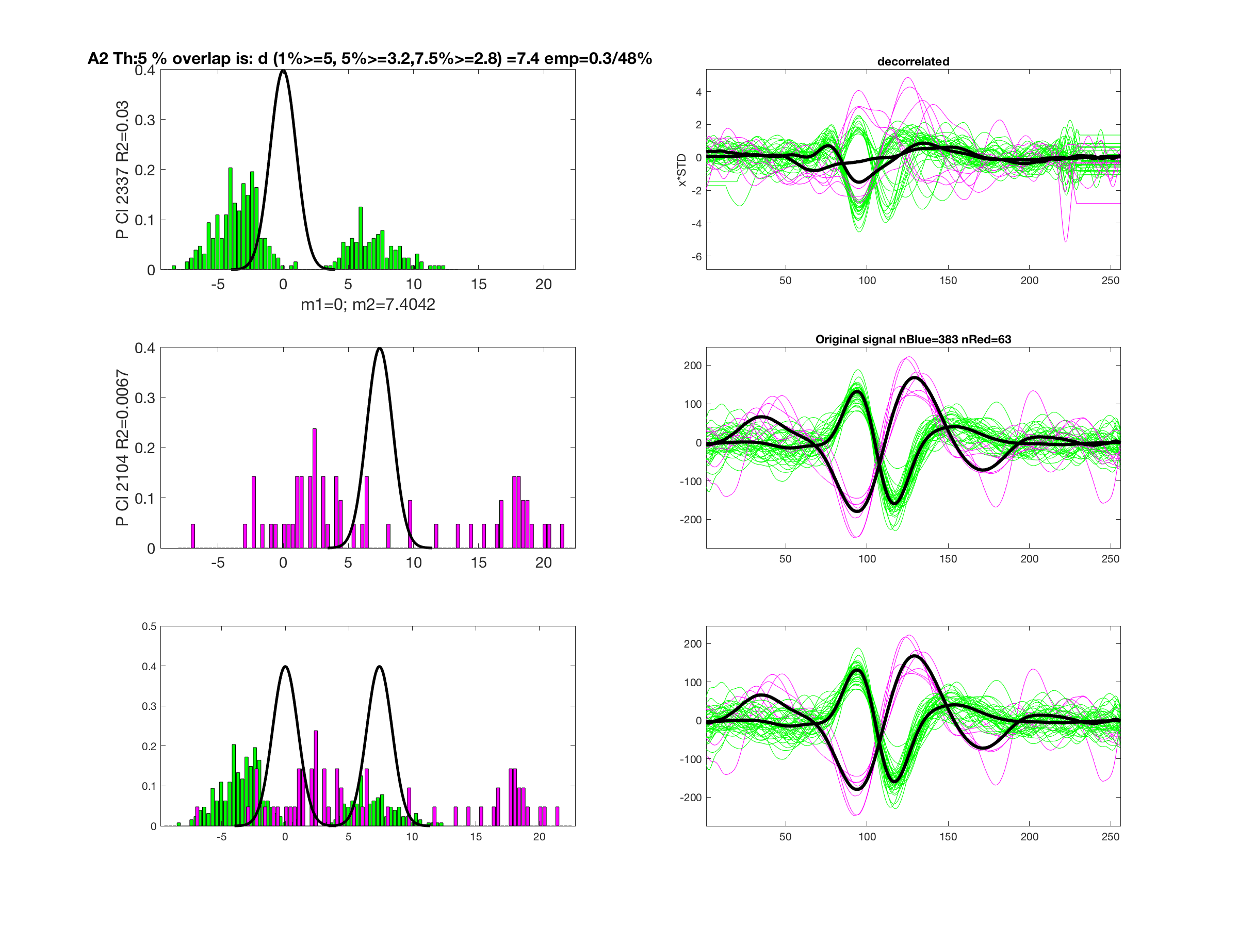
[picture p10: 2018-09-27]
Compression/Mess/5/A2_SepTest_2337_2104_THM_1.png

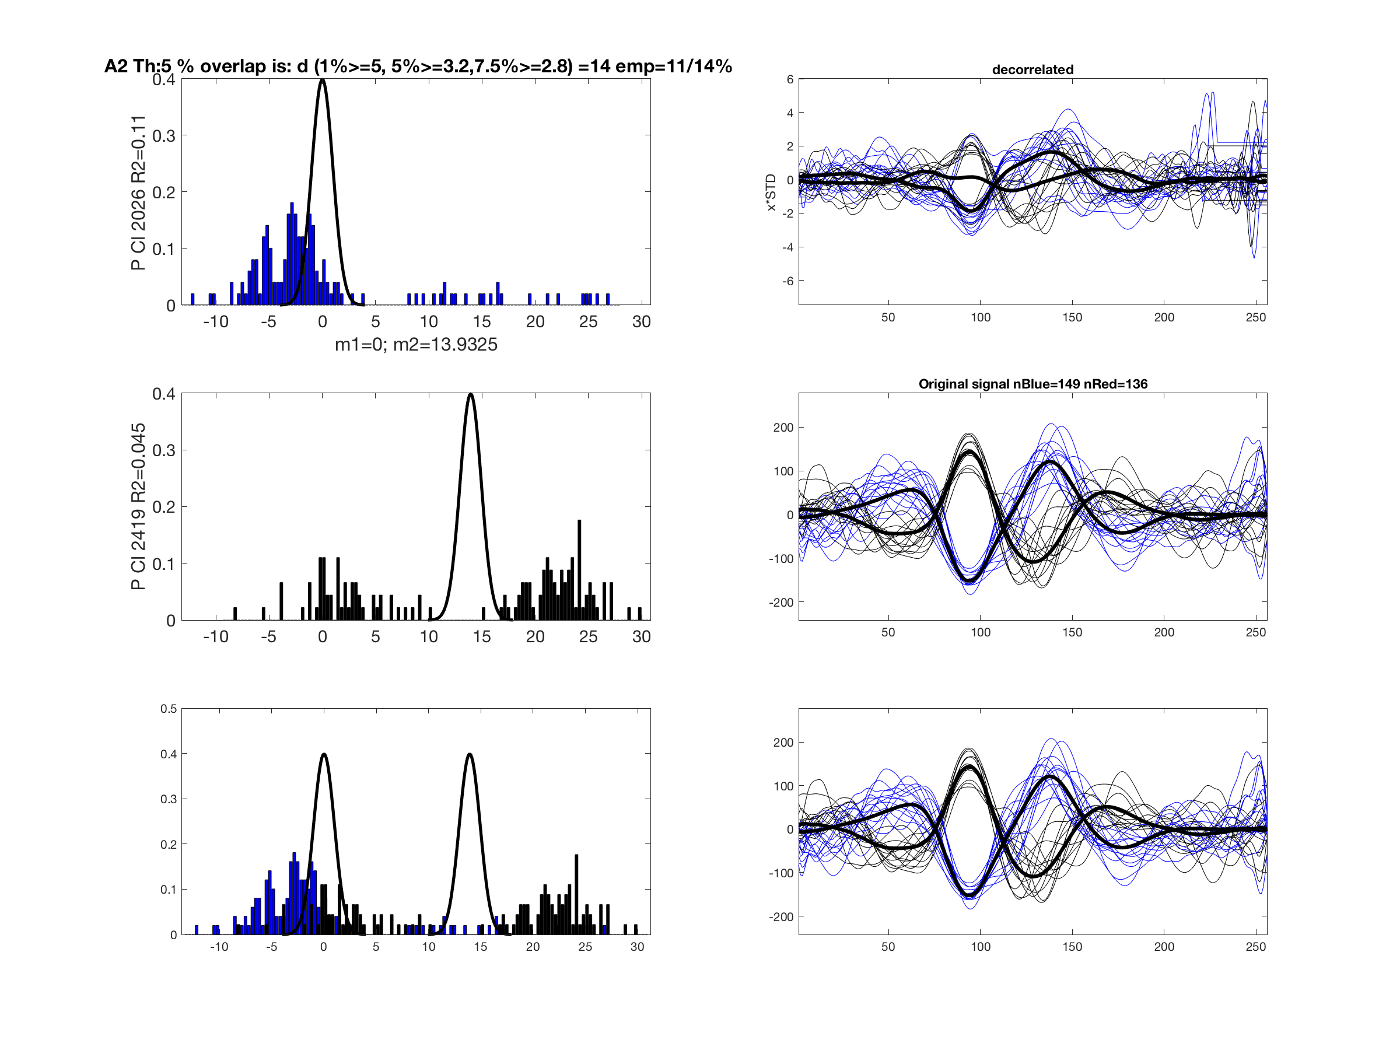
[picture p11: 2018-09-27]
Compression/Mess/5/A2_SepTest_2026_2419_THM_1.png

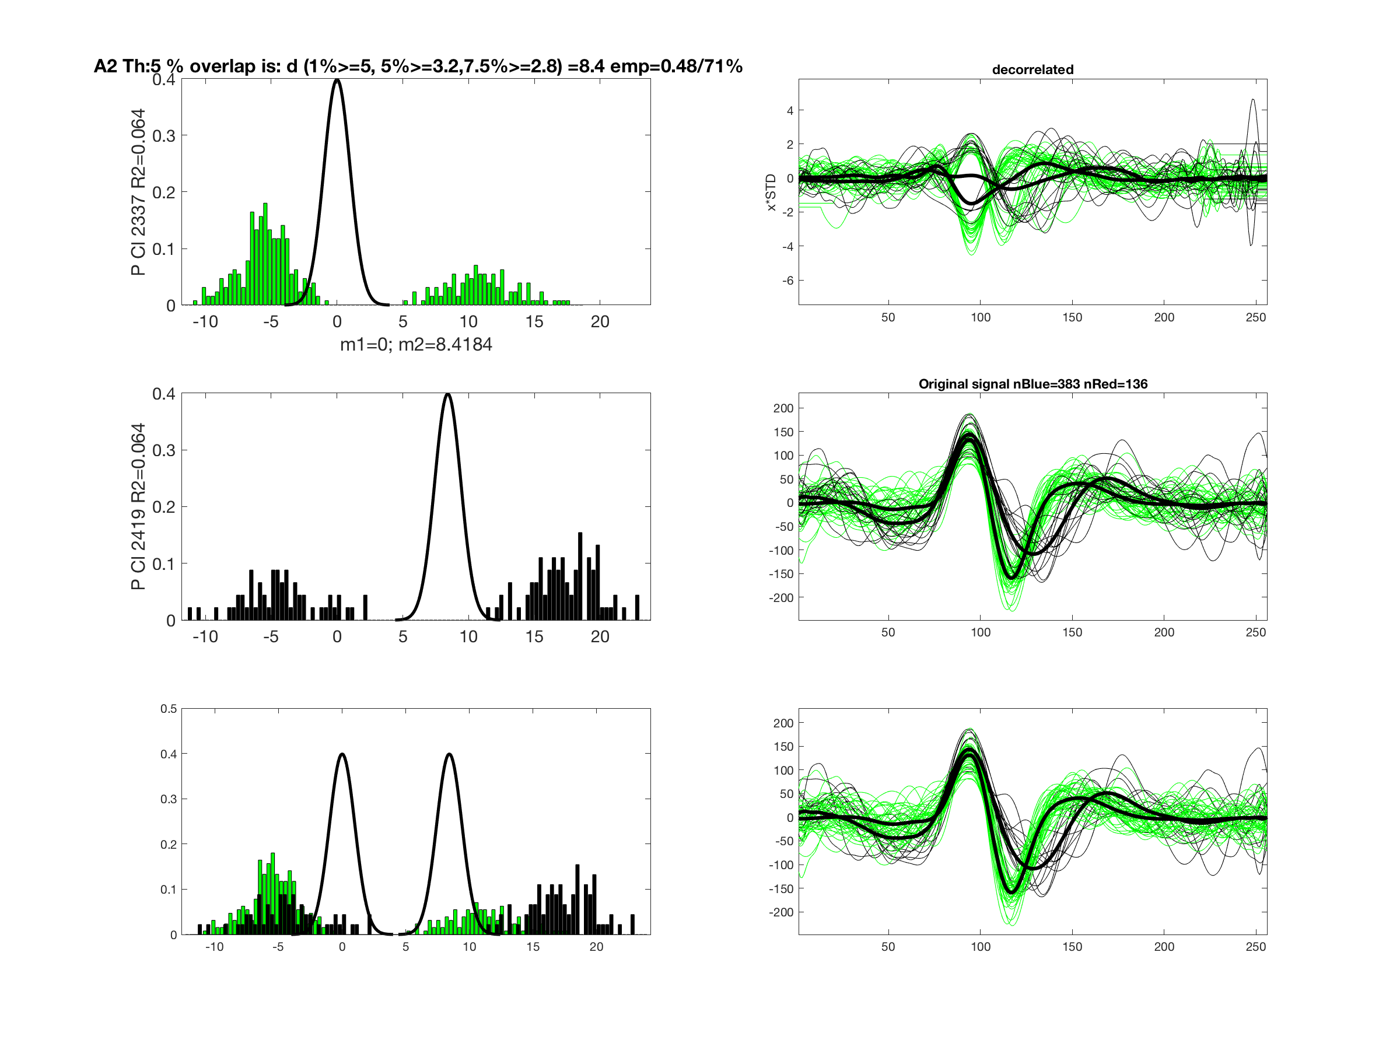
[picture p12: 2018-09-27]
Compression/Mess/5/A2_SepTest_2337_2419_THM_1.png

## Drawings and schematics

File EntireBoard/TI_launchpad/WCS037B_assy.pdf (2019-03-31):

# ART FILM - assembly_top

C46R353

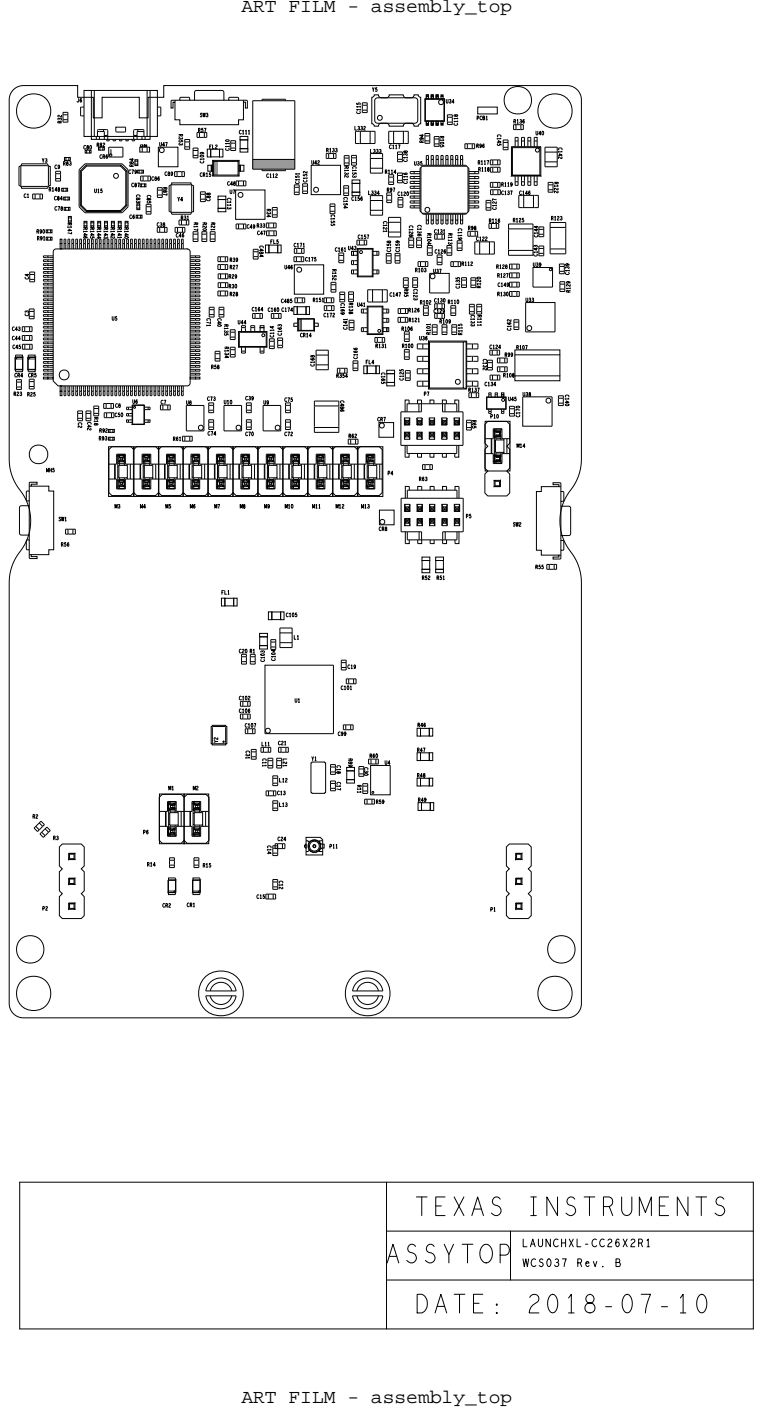
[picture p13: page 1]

TEXAS INSTRUMENTS

ASSYTOP | LAUNCHXL-CC26X2R1 WCS037 Rev. B

# ART FILM - assembly_bottom_mirrored

M16

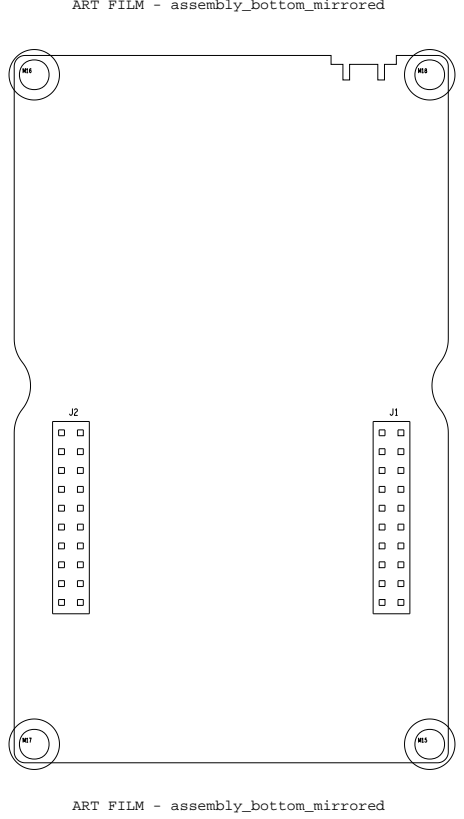
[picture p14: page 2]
ART FILM - assembly_bottom_mirrored

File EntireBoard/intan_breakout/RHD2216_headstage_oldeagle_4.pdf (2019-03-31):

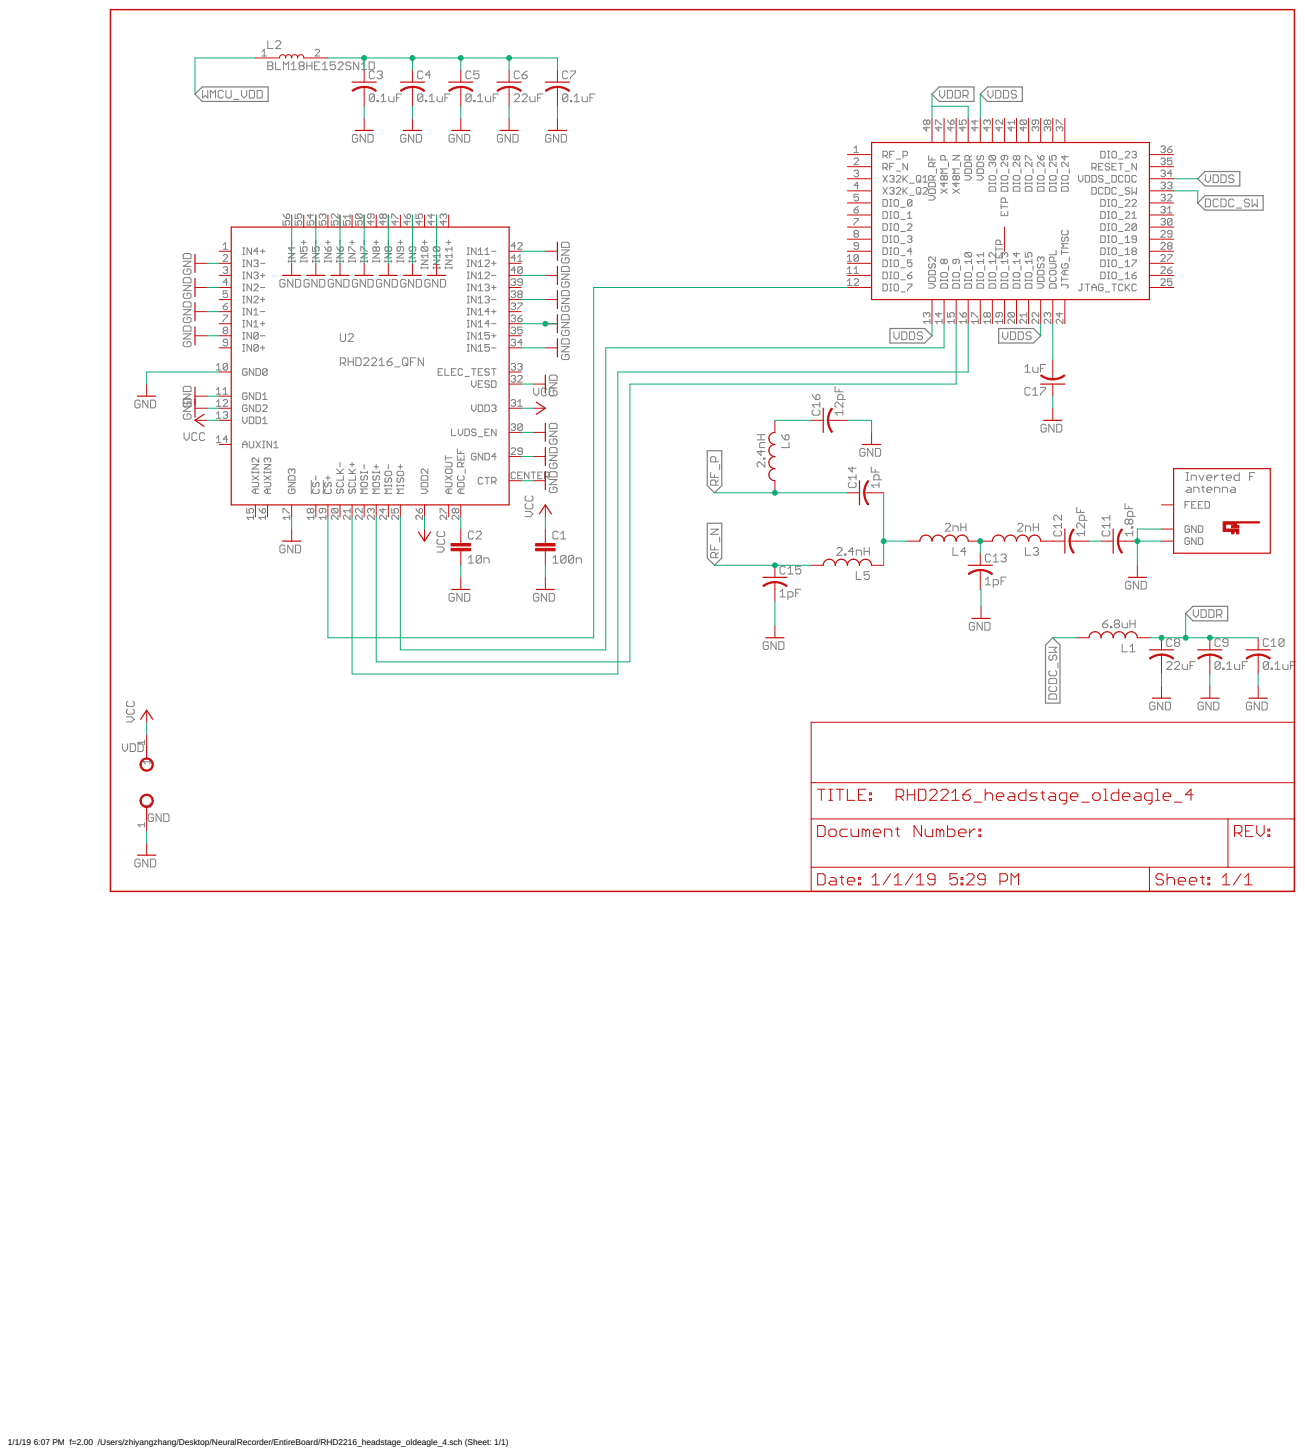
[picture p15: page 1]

1/1/19 6:07 PM f=2.00 /Users/zhiyangzhang/Desktop/NeuralRecorder/EntireBoard/RHD2216_headstage_oldeagle_4.sch (Sheet: 1/1)

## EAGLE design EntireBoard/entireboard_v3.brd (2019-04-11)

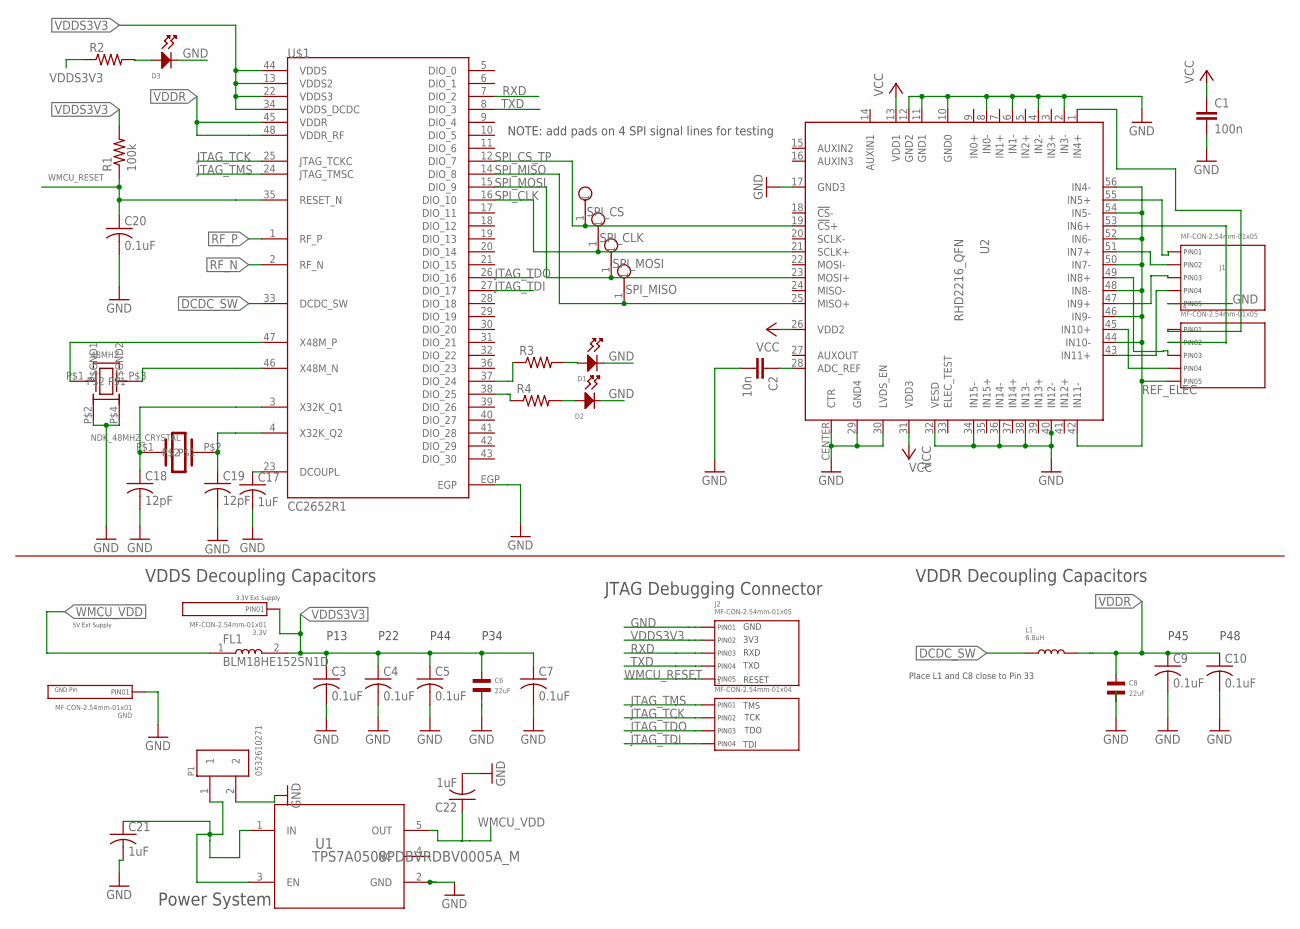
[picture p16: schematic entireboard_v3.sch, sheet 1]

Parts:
3.3V: MF-CON-2.54mm-01x01; PTH_2.54MM_01X01
38.768KHZ: EPSON_32.768KHZ_CRYSTAL; 2-SMD
48MHZ: NDK_48MHZ_CRYSTAL; 4-SMD
C1: 100n; 0402
C2: 10n; 0402
C3, C4, C5, C7, C9, C10, C20: 0.1uF; C0402
C6, C8: 22uF; C0603
C17, C21, C22: 1uF; C0402
C18, C19: 12pF; C0402
D1, D2, D3: LED_SINGLE-0603; LED0603
FL1: BLM18HE152SN1D; INDC1608X95
GND: MF-CON-2.54mm-01x01; PTH_2.54MM_01X01
J1, J2, J4: MF-CON-2.54mm-01x05; PTH_2.54MM_01X05
J3: MF-CON-2.54mm-01x04; PTH_2.54MM_01X04
L1: 6.8uH; L0603
P1: 0532610271; MOLEX_0532610271
R1: 100k; R0402
R2, R3, R4: R-US_R0402; R0402
SPI_CLK: RHD2000_EVAL_BOARD_TESTPOINT_SMALL
SPI_CS: RHD2000_EVAL_BOARD_TESTPOINT_SMALL
SPI_MISO: RHD2000_EVAL_BOARD_TESTPOINT_SMALL
SPI_MOSI: RHD2000_EVAL_BOARD_TESTPOINT_SMALL
U1: TPS7A0508PDBVRDBV0005A_M; DBV0005A_M
U2: RHD2216_QFN; QFN56_8_X_8_LARGE
U$1: CC2652R1; CC2652R1_QFN-48

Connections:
DCDC_SW: L1.P$1, U$1.33 (DCDC_SW)
GND: 48MHZ.P$2 (P$GND1), 48MHZ.P$4 (P$GND2), C1.2, C2.2, C3.2, C4.2, C5.2, C6.P$2, C7.2, C8.P$2, C9.2, C10.2, C17.2, C18.2, C19.2, C20.2, C21.2, C22.2, D1.CATHODE, D2.CATHODE, D3.CATHODE, GND.P$1, J1.P$5 (PIN5), J2.P$1 (PIN1), P1.2, U1.2 (GND), U2.2 (IN3-), U2.4 (IN2-), U2.6 (IN1-), U2.8 (IN0-), U2.10 (GND0), U2.11 (GND1), U2.12 (GND2), U2.17 (GND3), U2.29 (GND4), U2.30 (LVDS_EN), U2.32 (VESD), U2.34 (IN15-), U2.36 (IN14-), U2.38 (IN13-), U2.40 (IN12-), U2.CENTER (CTR), U$1.EGP; also elsewhere on the board
JTAG_TCK: J3.P$2 (PIN2), U$1.25 (JTAG_TCKC)
JTAG_TDI: J3.P$4 (PIN4), U$1.27 (DIO_17)
JTAG_TDO: J3.P$3 (PIN3), U$1.26 (DIO_16)
JTAG_TMS: J3.P$1 (PIN1), U$1.24 (JTAG_TMSC)
unnamed: C17.1, U$1.23 (DCOUPL)
unnamed: D1.ANODE, R3.2
unnamed: 48MHZ.P$1, U$1.47 (X48M_P)
unnamed: 48MHZ.P$3, U$1.46 (X48M_N)
unnamed: 38.768KHZ.P$1, C18.1, U$1.3 (X32K_Q1)
unnamed: 38.768KHZ.P$2, C19.1, U$1.4 (X32K_Q2)
unnamed: R4.1, U$1.38 (DIO_25)
unnamed: C21.1, P1.1, U1.1 (IN), U1.3 (EN)
unnamed: D2.ANODE, R4.2
unnamed: D3.ANODE, R2.2
unnamed: R3.1, U$1.37 (DIO_24)
unnamed: J1.P$4 (PIN4), U2.43 (IN11+)
unnamed: J4.P$4 (PIN4), U2.45 (IN10+)
unnamed: J1.P$3 (PIN3), U2.47 (IN9+)
unnamed: J4.P$3 (PIN3), U2.49 (IN8+)
unnamed: J1.P$2 (PIN2), U2.51 (IN7+)
unnamed: J4.P$2 (PIN2), U2.53 (IN6+)
unnamed: J1.P$1 (PIN1), U2.55 (IN5+)
unnamed: J4.P$1 (PIN1), U2.1 (IN4+)
unnamed: C2.1, U2.28 (ADC_REF)
NC: U1.4 (NC)
REF_ELEC: J4.P$5 (PIN5), U2.42 (IN11-), U2.44 (IN10-), U2.46 (IN9-), U2.48 (IN8-), U2.50 (IN7-), U2.52 (IN6-), U2.54 (IN5-), U2.56 (IN4-)
RF_N: U$1.2 (RF_N); also elsewhere on the board
RF_P: U$1.1 (RF_P); also elsewhere on the board
RXD: J2.P$3 (PIN3), U$1.7 (DIO_2)
SPI_CLK: SPI_CLK.1, U2.21 (SCLK+), U$1.16 (DIO_10)
SPI_CS_TP: SPI_CS.1, U2.19 (!CS!+), U$1.12 (DIO_7)
SPI_MISO: SPI_MISO.1, U2.25 (MISO+), U$1.14 (DIO_8)
SPI_MOSI: SPI_MOSI.1, U2.23 (MOSI+), U$1.15 (DIO_9)
TXD: J2.P$4 (PIN4), U$1.8 (DIO_3)
VCC: C1.1, U2.13 (VDD1), U2.26 (VDD2), U2.31 (VDD3)
VDDR: C8.P$1, C9.1, C10.1, L1.P$2, U$1.45 (VDDR), U$1.48 (VDDR_RF)
VDDS3V3: 3.3V.P$1, C3.1, C4.1, C5.1, C6.P$1, C7.1, FL1.2, J2.P$2 (PIN2), R1.2, R2.1, U$1.13 (VDDS2), U$1.22 (VDDS3), U$1.34 (VDDS_DCDC), U$1.44 (VDDS)
WMCU_RESET: C20.1, J2.P$5 (PIN5), R1.1, U$1.35 (RESET_N)
WMCU_VDD: C22.1, FL1.1, U1.5 (OUT)

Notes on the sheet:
VDDS Decoupling Capacitors
VDDR Decoupling Capacitors
Place L1 and C8 close to Pin 33
P45
P48
P13
P22
P44
P34
JTAG Debugging Connector
NOTE: add pads on 4 SPI signal lines for testing
5V Ext Supply
3.3V Ext Supply
GND Pin
Power System
GND
3V3
RXD
TXD
TMS
TCK
TDI
TDO
RESET

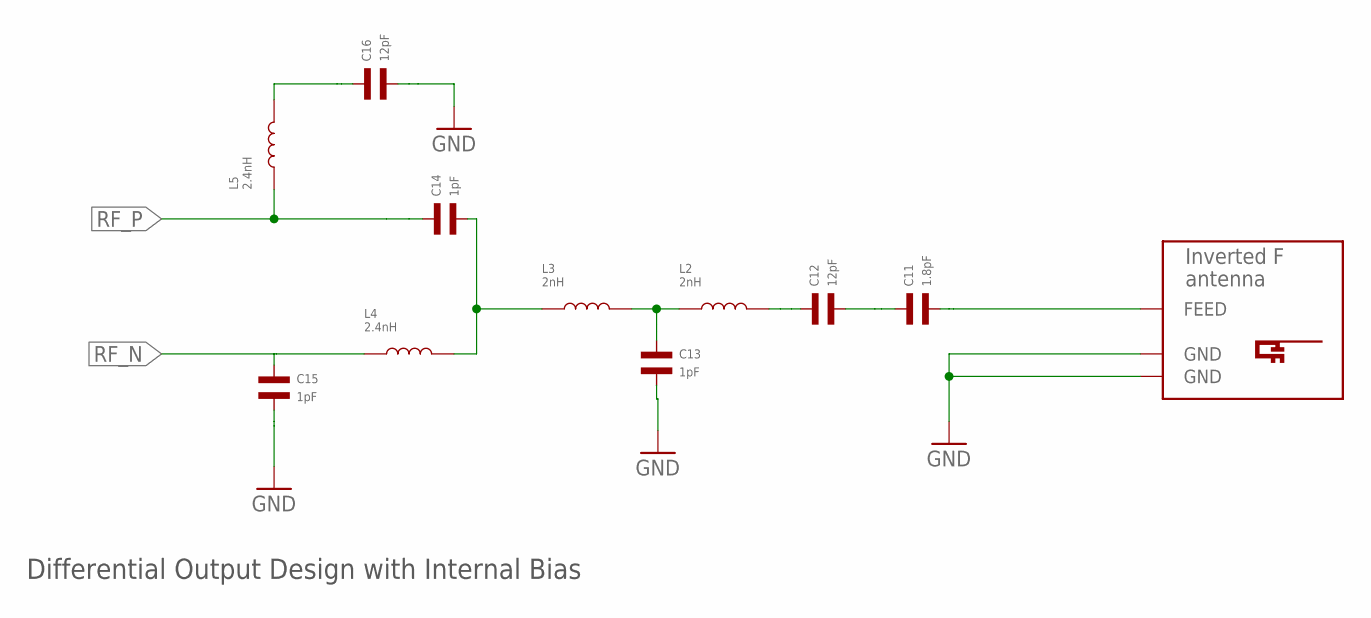
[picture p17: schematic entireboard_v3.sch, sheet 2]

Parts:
C11: 1.8pF; C0402
C12, C16: 12pF; C0402
C13, C14, C15: 1pF; C0402
L2, L3: 2nH; L0402
L4, L5: 2.4nH; L0402
U$2: INVERTED_F_ANTENNA+0; DN007+0

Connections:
GND: C13.P$2, C15.P$2, C16.P$2, U$2.GND, U$2.GND@1 (GND); also elsewhere on the board
unnamed: C11.P$1, C12.P$2
unnamed: C12.P$1, L2.P$2
unnamed: C13.P$1, L2.P$1, L3.P$2
unnamed: C14.P$2, L3.P$1, L4.P$2
unnamed: C11.P$2, U$2.FEED
unnamed: C16.P$1, L5.P$2
RF_N: C15.P$1, L4.P$1; also elsewhere on the board
RF_P: C14.P$1, L5.P$1; also elsewhere on the board

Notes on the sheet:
Differential Output Design with Internal Bias

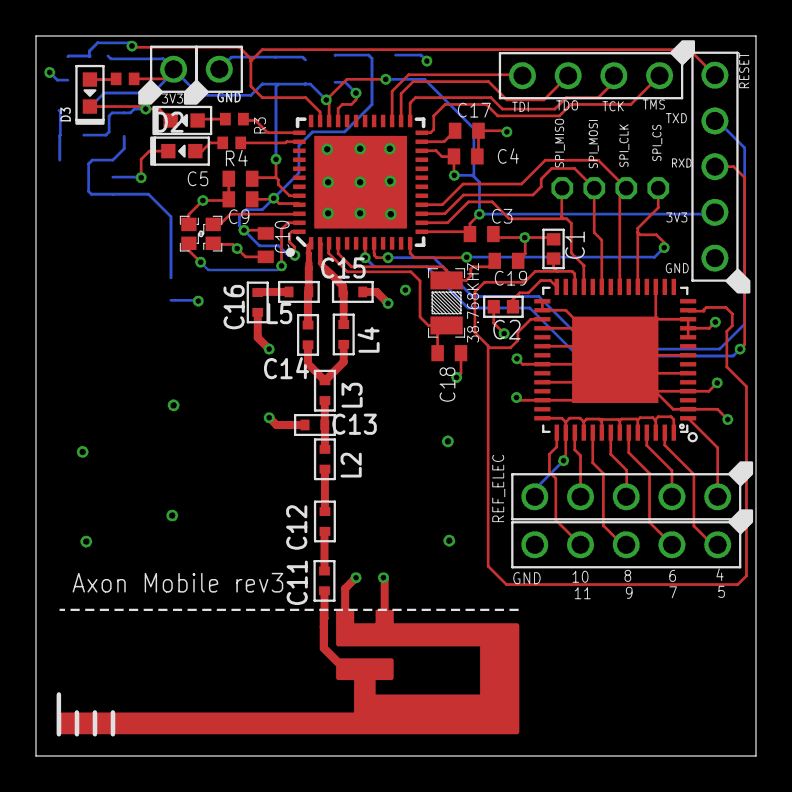
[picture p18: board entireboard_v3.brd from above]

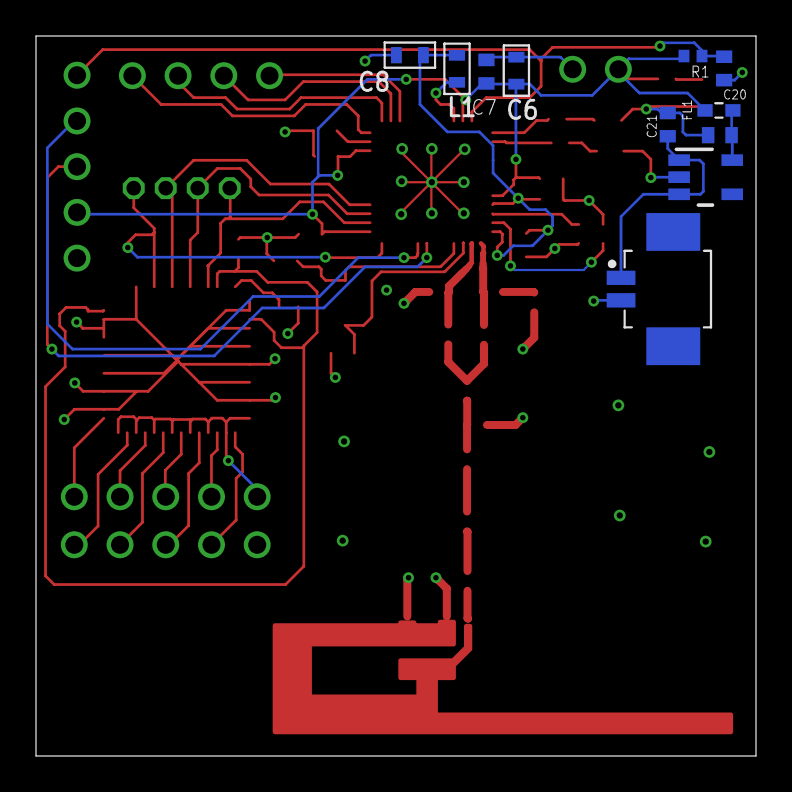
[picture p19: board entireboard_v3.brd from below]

Board: 4 copper layers, 40.0 x 40.0 mm, 52 parts (11 on the bottom side), 46 nets.

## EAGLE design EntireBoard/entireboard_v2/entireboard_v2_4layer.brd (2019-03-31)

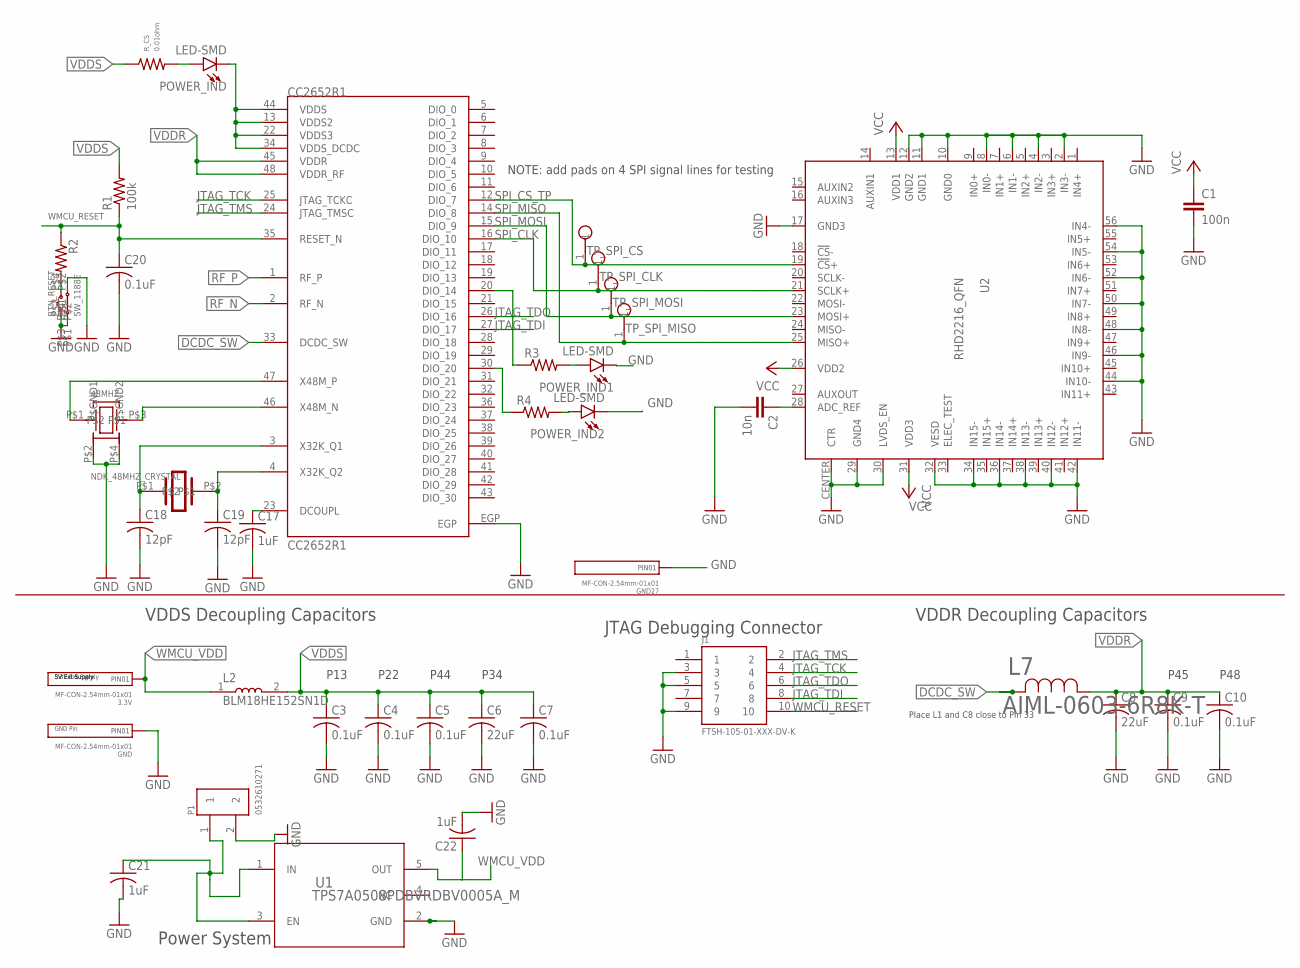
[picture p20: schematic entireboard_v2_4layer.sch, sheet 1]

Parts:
3.3V: MF-CON-2.54mm-01x01; PTH_2.54MM_01X01
38.768KHZ: EPSON_32.768KHZ_CRYSTAL; 2-SMD
48MHZ: NDK_48MHZ_CRYSTAL; 4-SMD
BTN_RESET: SW_1188E
C1: 100n; 0402
C2: 10n; 0402
C3, C4, C5, C7, C9, C10, C20: 0.1uF; C0402
C6, C8: 22uF; C0402
C17, C21, C22: 1uF; C0402
C18, C19: 12pF; C0402
CC2652R1: CC2652R1; CC2652R1_QFN-48
GND, GND27: MF-CON-2.54mm-01x01; PTH_2.54MM_01X01
J1: FTSH-105-01-XXX-DV-K
L2: BLM18HE152SN1D; INDC1608X95
L7: AIML-0603-6R8K-T; AIML-0603
P1: 0532610271; MOLEX_0532610271
POWER_IND, POWER_IND1, POWER_IND2: LED-SMD; RHD2000_EVAL_BOARD_0402
R1: 100k; R0402
R2, R3, R4: R-US_R0402; R0402
R_CS: 0.01ohm; R0402
TP_SPI_CLK: RHD2000_EVAL_BOARD_TESTPOINT_SMALL
TP_SPI_CS: RHD2000_EVAL_BOARD_TESTPOINT_SMALL
TP_SPI_MISO: RHD2000_EVAL_BOARD_TESTPOINT_SMALL
TP_SPI_MOSI: RHD2000_EVAL_BOARD_TESTPOINT_SMALL
U1: TPS7A0508PDBVRDBV0005A_M; DBV0005A_M
U2: RHD2216_QFN; QFN56_8_X_8_LARGE

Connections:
DCDC_SW: CC2652R1.33 (DCDC_SW), L7.2
GND: 48MHZ.P$2 (P$GND1), 48MHZ.P$4 (P$GND2), BTN_RESET.P$1, BTN_RESET.P$2, BTN_RESET.P$3, C1.2, C2.2, C3.2, C4.2, C5.2, C6.2, C7.2, C8.2, C9.2, C10.2, C17.2, C18.2, C19.2, C20.2, C21.2, C22.2, CC2652R1.EGP, GND.P$1, GND27.P$1, J1.3, J1.5, J1.9, P1.2, POWER_IND1.2 (C), POWER_IND2.2 (C), U1.2 (GND), U2.2 (IN3-), U2.4 (IN2-), U2.6 (IN1-), U2.8 (IN0-), U2.10 (GND0), U2.11 (GND1), U2.12 (GND2), U2.17 (GND3), U2.29 (GND4), U2.30 (LVDS_EN), U2.32 (VESD), U2.34 (IN15-), U2.36 (IN14-), U2.38 (IN13-), U2.40 (IN12-), U2.42 (IN11-), U2.44 (IN10-), U2.46 (IN9-), U2.48 (IN8-), U2.50 (IN7-), U2.52 (IN6-), U2.54 (IN5-), U2.56 (IN4-), U2.CENTER (CTR); also elsewhere on the board
JTAG_TCK: CC2652R1.25 (JTAG_TCKC), J1.4
JTAG_TDI: CC2652R1.27 (DIO_17), J1.8
JTAG_TDO: CC2652R1.26 (DIO_16), J1.6
JTAG_TMS: CC2652R1.24 (JTAG_TMSC), J1.2
unnamed: C17.1, CC2652R1.23 (DCOUPL)
unnamed: 48MHZ.P$1, CC2652R1.47 (X48M_P)
unnamed: 48MHZ.P$3, CC2652R1.46 (X48M_N)
unnamed: 38.768KHZ.P$1, C18.1, CC2652R1.3 (X32K_Q1)
unnamed: 38.768KHZ.P$2, C19.1, CC2652R1.4 (X32K_Q2)
unnamed: POWER_IND.1 (A), R_CS.P$2
unnamed: C21.1, P1.1, U1.1 (IN), U1.3 (EN)
unnamed: BTN_RESET.P$4, R2.2
unnamed: CC2652R1.20 (DIO_14), R3.1
unnamed: POWER_IND1.1 (A), R3.2
unnamed: CC2652R1.30 (DIO_20), R4.1
unnamed: POWER_IND2.1 (A), R4.2
unnamed: C2.1, U2.28 (ADC_REF)
NC: U1.4 (NC)
RF_N: CC2652R1.2 (RF_N); also elsewhere on the board
RF_P: CC2652R1.1 (RF_P); also elsewhere on the board
SPI_CLK: CC2652R1.16 (DIO_10), TP_SPI_CLK.1, U2.21 (SCLK+)
SPI_CS_TP: CC2652R1.12 (DIO_7), TP_SPI_CS.1, U2.19 (!CS!+)
SPI_MISO: CC2652R1.14 (DIO_8), TP_SPI_MISO.1, U2.25 (MISO+)
SPI_MOSI: CC2652R1.15 (DIO_9), TP_SPI_MOSI.1, U2.23 (MOSI+)
VCC: C1.1, U2.13 (VDD1), U2.26 (VDD2), U2.31 (VDD3)
VDDR: C8.1, C9.1, C10.1, CC2652R1.45 (VDDR), CC2652R1.48 (VDDR_RF), L7.1
VDDS: C3.1, C4.1, C5.1, C6.1, C7.1, CC2652R1.13 (VDDS2), CC2652R1.22 (VDDS3), CC2652R1.34 (VDDS_DCDC), CC2652R1.44 (VDDS), L2.2, POWER_IND.2 (C), R1.2, R_CS.P$1
WMCU_RESET: C20.1, CC2652R1.35 (RESET_N), J1.10, R1.1, R2.1
WMCU_VDD: 3.3V.P$1, C22.1, L2.1, U1.5 (OUT)

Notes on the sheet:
VDDS Decoupling Capacitors
VDDR Decoupling Capacitors
Place L1 and C8 close to Pin 33
P45
P48
P13
P22
P44
P34
JTAG Debugging Connector
NOTE: add pads on 4 SPI signal lines for testing
5V Ext Supply
3.3V Ext Supply
GND Pin
Power System

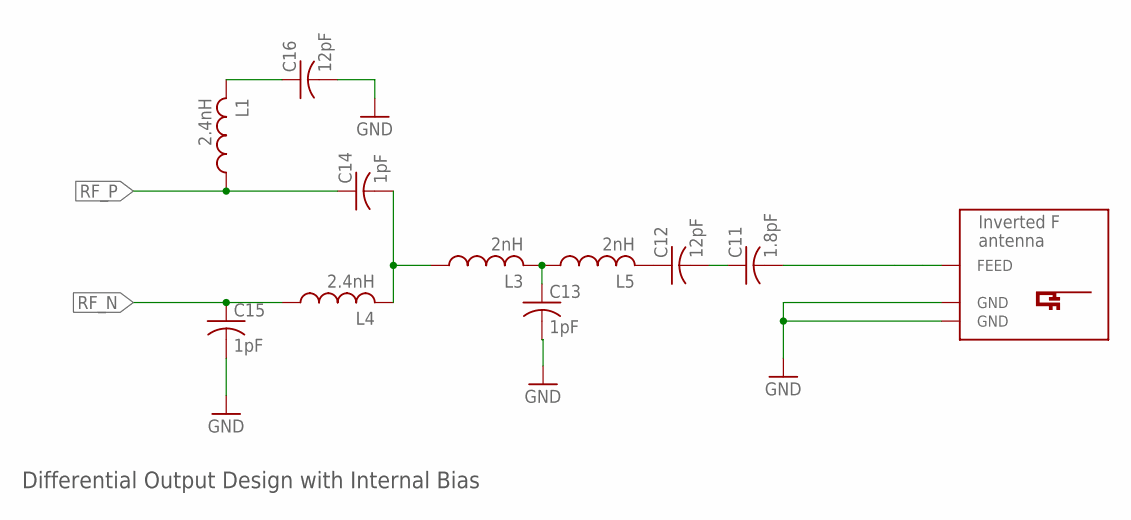
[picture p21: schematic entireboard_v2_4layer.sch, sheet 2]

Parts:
C11: 1.8pF; C0402
C12, C16: 12pF; C0402
C13, C14, C15: 1pF; C0402
L1, L4: 2.4nH; L0201
L3, L5: 2nH; L0201
U$2: INVERTED_F_ANTENNA+0; DN007+0

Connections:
GND: C13.2, C15.2, C16.2, U$2.GND, U$2.GND@1 (GND); also elsewhere on the board
unnamed: C11.1, C12.2
unnamed: C12.1, L5.2
unnamed: C13.1, L3.2, L5.1
unnamed: C14.2, L3.1, L4.2
unnamed: C11.2, U$2.FEED
unnamed: C16.1, L1.2
RF_N: C15.1, L4.1; also elsewhere on the board
RF_P: C14.1, L1.1; also elsewhere on the board

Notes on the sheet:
Differential Output Design with Internal Bias

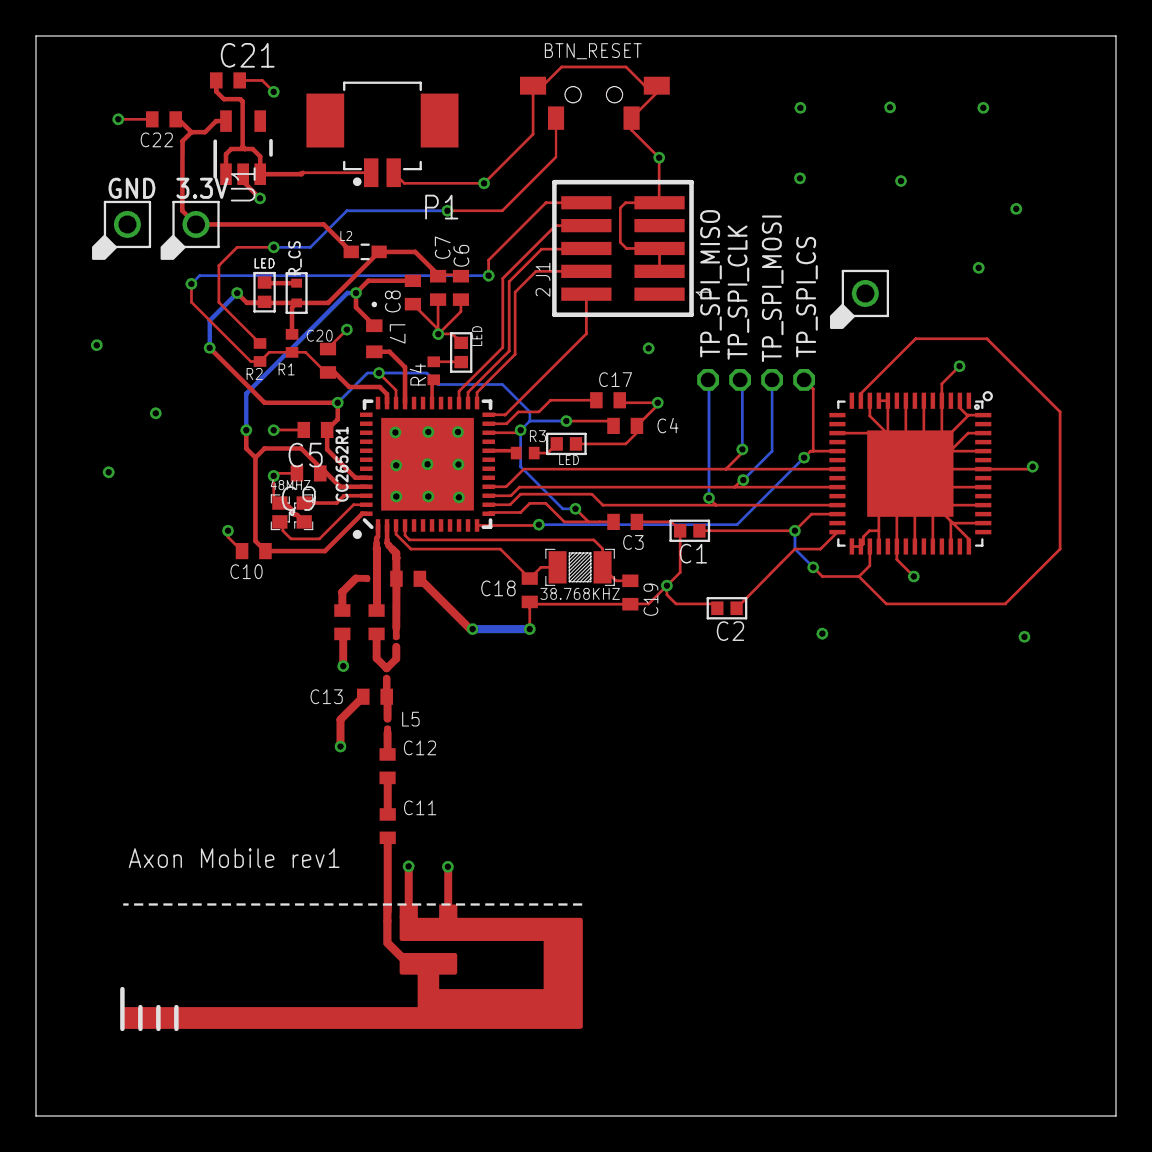
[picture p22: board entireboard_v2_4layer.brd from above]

Board: 4 copper layers, 60.0 x 60.0 mm, 52 parts (0 on the bottom side), 36 nets.

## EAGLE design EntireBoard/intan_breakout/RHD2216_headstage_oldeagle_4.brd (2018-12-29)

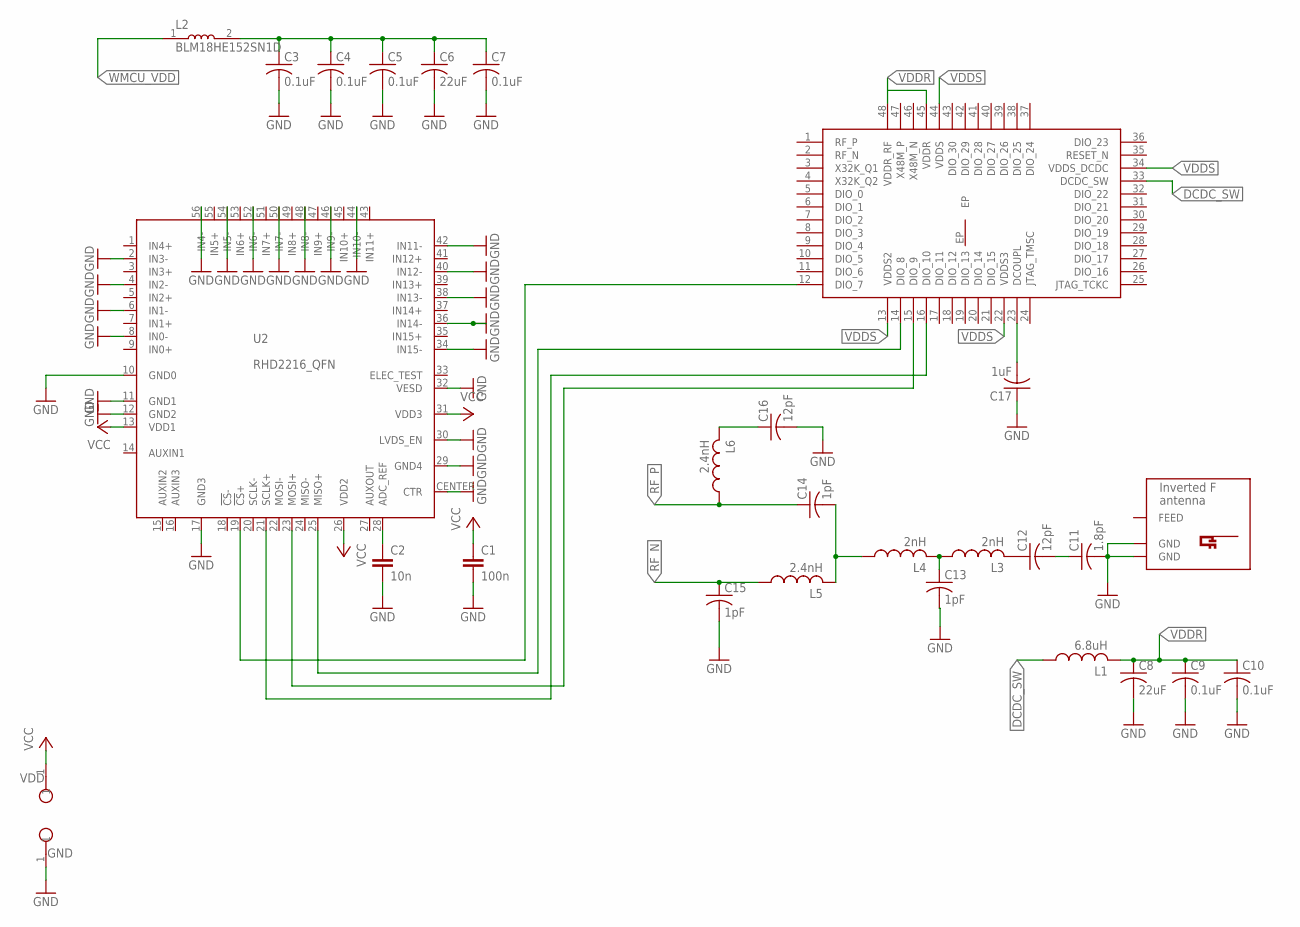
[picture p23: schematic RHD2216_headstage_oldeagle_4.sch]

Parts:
C1: 100n; 0402
C2: 10n; 0402
C3, C4, C5, C7, C9, C10: 0.1uF; C0402
C6, C8: 22uF; C0402
C11: 1.8pF; C0402
C12, C16: 12pF; C0402
C13, C14, C15: 1pF; C0402
C17: 1uF; C0402
GND: TESTPOINT_SMALL
L1: 6.8uH; 0204/5
L2: BLM18HE152SN1D; INDC1608X95
L3, L4: 2nH; 0204/5
L5, L6: 2.4nH; 0204/5
U2: RHD2216_QFN; QFN56_8_X_8_LARGE
U$1: CC2652R1; QFN-48
U$2: INVERTED_F_ANTENNA+0; DN007+0
VDD: TESTPOINT_SMALL

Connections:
DCDC_SW: L1.1, U$1.33 (DCDC_SW)
GND: C1.2, C2.2, C3.2, C4.2, C5.2, C6.2, C7.2, C8.2, C9.2, C10.2, C11.2, C13.2, C15.2, C16.2, C17.1, GND.1, U2.2 (IN3-), U2.4 (IN2-), U2.6 (IN1-), U2.8 (IN0-), U2.10 (GND0), U2.11 (GND1), U2.12 (GND2), U2.17 (GND3), U2.29 (GND4), U2.30 (LVDS_EN), U2.32 (VESD), U2.34 (IN15-), U2.36 (IN14-), U2.38 (IN13-), U2.40 (IN12-), U2.42 (IN11-), U2.44 (IN10-), U2.46 (IN9-), U2.48 (IN8-), U2.50 (IN7-), U2.52 (IN6-), U2.54 (IN5-), U2.56 (IN4-), U2.CENTER (CTR), U$2.GND, U$2.GND@1 (GND)
unnamed: U2.23 (MOSI+), U$1.15 (DIO_9)
unnamed: U2.25 (MISO+), U$1.14 (DIO_8)
unnamed: U2.19 (!CS!+), U$1.12 (DIO_7)
unnamed: U2.21 (SCLK+), U$1.16 (DIO_10)
unnamed: C3.1, C4.1, C5.1, C6.1, C7.1, L2.2
unnamed: C11.1, C12.2
unnamed: C12.1, L3.2
unnamed: C13.1, L3.1, L4.2
unnamed: C14.2, L4.1, L5.2
unnamed: C17.2, U$1.23 (DCOUPL)
unnamed: C16.1, L6.2
unnamed: C2.1, U2.28 (ADC_REF)
RF_N: C15.1, L5.1
RF_P: C14.1, L6.1
VCC: C1.1, U2.13 (VDD1), U2.26 (VDD2), U2.31 (VDD3), VDD.1
VDDR: C8.1, C9.1, C10.1, L1.2, U$1.45 (VDDR), U$1.48 (VDDR_RF)
VDDS: U$1.13 (VDDS2), U$1.22 (VDDS3), U$1.34 (VDDS_DCDC), U$1.44 (VDDS)
WMCU_VDD: L2.1

Board: 2 copper layers, 28 parts (0 on the bottom side), 19 nets, no tracks yet.

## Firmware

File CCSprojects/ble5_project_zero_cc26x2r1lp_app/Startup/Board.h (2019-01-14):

/*
 * Copyright (c) 2015-2018, Texas Instruments Incorporated
 * All rights reserved.
 *
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
 * *  Redistributions of source code must retain the above copyright
 *    notice, this list of conditions and the following disclaimer.
 *
 * *  Redistributions in binary form must reproduce the above copyright
 *    notice, this list of conditions and the following disclaimer in the
 *    documentation and/or other materials provided with the distribution.
 *
 * *  Neither the name of Texas Instruments Incorporated nor the names of
 *    its contributors may be used to endorse or promote products derived
 *    from this software without specific prior written permission.
 *
 * THIS SOFTWARE IS PROVIDED BY THE COPYRIGHT HOLDERS AND CONTRIBUTORS "AS IS"
 * AND ANY EXPRESS OR IMPLIED WARRANTIES, INCLUDING, BUT NOT LIMITED TO,
 * THE IMPLIED WARRANTIES OF MERCHANTABILITY AND FITNESS FOR A PARTICULAR
 * PURPOSE ARE DISCLAIMED. IN NO EVENT SHALL THE COPYRIGHT OWNER OR
 * CONTRIBUTORS BE LIABLE FOR ANY DIRECT, INDIRECT, INCIDENTAL, SPECIAL,
 * EXEMPLARY, OR CONSEQUENTIAL DAMAGES (INCLUDING, BUT NOT LIMITED TO,
 * PROCUREMENT OF SUBSTITUTE GOODS OR SERVICES; LOSS OF USE, DATA, OR PROFITS;
 * OR BUSINESS INTERRUPTION) HOWEVER CAUSED AND ON ANY THEORY OF LIABILITY,
 * WHETHER IN CONTRACT, STRICT LIABILITY, OR TORT (INCLUDING NEGLIGENCE OR
 * OTHERWISE) ARISING IN ANY WAY OUT OF THE USE OF THIS SOFTWARE,
 * EVEN IF ADVISED OF THE POSSIBILITY OF SUCH DAMAGE.
 */

#ifndef __BOARD_H
#define __BOARD_H

#define Board_CC26X2R1_LAUNCHXL

#ifdef __cplusplus
extern "C" {
#endif

#include "CC26X2R1_LAUNCHXL.h"

#define Board_initGeneral()     CC26X2R1_LAUNCHXL_initGeneral()

#define Board_shutDownExtFlash() CC26X2R1_LAUNCHXL_shutDownExtFlash()

#define Board_wakeUpExtFlash() CC26X2R1_LAUNCHXL_wakeUpExtFlash()

/* These #defines allow us to reuse TI-RTOS across other device families */

#define Board_ADC0              CC26X2R1_LAUNCHXL_ADC0
#define Board_ADC1              CC26X2R1_LAUNCHXL_ADC1

#define Board_ADCBUF0           CC26X2R1_LAUNCHXL_ADCBUF0
#define Board_ADCBUF0CHANNEL0   CC26X2R1_LAUNCHXL_ADCBUF0CHANNEL0
#define Board_ADCBUF0CHANNEL1   CC26X2R1_LAUNCHXL_ADCBUF0CHANNEL1

#define Board_ECDH0             CC26X2R1_LAUNCHXL_ECDH0
#define Board_ECDSA0            CC26X2R1_LAUNCHXL_ECDSA0
#define Board_ECJPAKE0          CC26X2R1_LAUNCHXL_ECJPAKE0
#define Board_AESCCM0           CC26X2R1_LAUNCHXL_AESCCM0
#define Board_AESCBC0           CC26X2R1_LAUNCHXL_AESCBC0
#define Board_AESECB0           CC26X2R1_LAUNCHXL_AESECB0
#define Board_SHA20             CC26X2R1_LAUNCHXL_SHA20

#define Board_DIO0              CC26X2R1_LAUNCHXL_DIO0
#define Board_DIO1_RFSW         CC26X2R1_LAUNCHXL_DIO1_RFSW
#define Board_DIO12             CC26X2R1_LAUNCHXL_DIO12
#define Board_DIO15             CC26X2R1_LAUNCHXL_DIO15
#define Board_DIO16_TDO         CC26X2R1_LAUNCHXL_DIO16_TDO
#define Board_DIO17_TDI         CC26X2R1_LAUNCHXL_DIO17_TDI
#define Board_DIO21             CC26X2R1_LAUNCHXL_DIO21
#define Board_DIO22             CC26X2R1_LAUNCHXL_DIO22

#define Board_DIO23_ANALOG      CC26X2R1_LAUNCHXL_DIO23_ANALOG
#define Board_DIO24_ANALOG      CC26X2R1_LAUNCHXL_DIO24_ANALOG
#define Board_DIO25_ANALOG      CC26X2R1_LAUNCHXL_DIO25_ANALOG
#define Board_DIO26_ANALOG      CC26X2R1_LAUNCHXL_DIO26_ANALOG
#define Board_DIO27_ANALOG      CC26X2R1_LAUNCHXL_DIO27_ANALOG
#define Board_DIO28_ANALOG      CC26X2R1_LAUNCHXL_DIO28_ANALOG
#define Board_DIO29_ANALOG      CC26X2R1_LAUNCHXL_DIO29_ANALOG
#define Board_DIO30_ANALOG      CC26X2R1_LAUNCHXL_DIO30_ANALOG

#define Board_GPIO_BUTTON0      CC26X2R1_LAUNCHXL_GPIO_S1
#define Board_GPIO_BUTTON1      CC26X2R1_LAUNCHXL_GPIO_S2
#define Board_GPIO_BTN1         CC26X2R1_LAUNCHXL_GPIO_S1
#define Board_GPIO_BTN2         CC26X2R1_LAUNCHXL_GPIO_S2
#define Board_GPIO_LED0         CC26X2R1_LAUNCHXL_GPIO_LED_RED
#define Board_GPIO_LED1         CC26X2R1_LAUNCHXL_GPIO_LED_GREEN
#define Board_GPIO_LED2         CC26X2R1_LAUNCHXL_GPIO_LED_RED
#define Board_GPIO_RLED         CC26X2R1_LAUNCHXL_GPIO_LED_RED
#define Board_GPIO_GLED         CC26X2R1_LAUNCHXL_GPIO_LED_GREEN
#define Board_GPIO_LED_ON       CC26X2R1_LAUNCHXL_GPIO_LED_ON
#define Board_GPIO_LED_OFF      CC26X2R1_LAUNCHXL_GPIO_LED_OFF

#define Board_GPTIMER0A         CC26X2R1_LAUNCHXL_GPTIMER0A
#define Board_GPTIMER0B         CC26X2R1_LAUNCHXL_GPTIMER0B
#define Board_GPTIMER1A         CC26X2R1_LAUNCHXL_GPTIMER1A
#define Board_GPTIMER1B         CC26X2R1_LAUNCHXL_GPTIMER1B
#define Board_GPTIMER2A         CC26X2R1_LAUNCHXL_GPTIMER2A
#define Board_GPTIMER2B         CC26X2R1_LAUNCHXL_GPTIMER2B
#define Board_GPTIMER3A         CC26X2R1_LAUNCHXL_GPTIMER3A
#define Board_GPTIMER3B         CC26X2R1_LAUNCHXL_GPTIMER3B

#define Board_I2C0              CC26X2R1_LAUNCHXL_I2C0
#define Board_I2C_TMP           Board_I2C0

#define Board_NVSINTERNAL       CC26X2R1_LAUNCHXL_NVSCC26XX0
#define Board_NVSEXTERNAL       CC26X2R1_LAUNCHXL_NVSSPI25X0

#define Board_PIN_BUTTON0       CC26X2R1_LAUNCHXL_PIN_BTN1
#define Board_PIN_BUTTON1       CC26X2R1_LAUNCHXL_PIN_BTN2
#define Board_PIN_BTN1          CC26X2R1_LAUNCHXL_PIN_BTN1
#define Board_PIN_BTN2          CC26X2R1_LAUNCHXL_PIN_BTN2
#define Board_PIN_LED0          CC26X2R1_LAUNCHXL_PIN_RLED
#define Board_PIN_LED1          CC26X2R1_LAUNCHXL_PIN_GLED
#define Board_PIN_LED2          CC26X2R1_LAUNCHXL_PIN_RLED
#define Board_PIN_RLED          CC26X2R1_LAUNCHXL_PIN_RLED
#define Board_PIN_GLED          CC26X2R1_LAUNCHXL_PIN_GLED

#define Board_PWM0              CC26X2R1_LAUNCHXL_PWM0
#define Board_PWM1              CC26X2R1_LAUNCHXL_PWM1
#define Board_PWM2              CC26X2R1_LAUNCHXL_PWM2
#define Board_PWM3              CC26X2R1_LAUNCHXL_PWM3
#define Board_PWM4              CC26X2R1_LAUNCHXL_PWM4
#define Board_PWM5              CC26X2R1_LAUNCHXL_PWM5
#define Board_PWM6              CC26X2R1_LAUNCHXL_PWM6
#define Board_PWM7              CC26X2R1_LAUNCHXL_PWM7

#define Board_SD0               CC26X2R1_LAUNCHXL_SDSPI0

#define Board_SPI0              CC26X2R1_LAUNCHXL_SPI0
#define Board_SPI1              CC26X2R1_LAUNCHXL_SPI1
#define Board_SPI_FLASH_CS      CC26X2R1_LAUNCHXL_SPI_FLASH_CS
#define Board_FLASH_CS_ON       0
#define Board_FLASH_CS_OFF      1

#define Board_SPI_MASTER        CC26X2R1_LAUNCHXL_SPI0
#define Board_SPI_SLAVE         CC26X2R1_LAUNCHXL_SPI0
#define Board_SPI_MASTER_READY  CC26X2R1_LAUNCHXL_SPI_MASTER_READY
#define Board_SPI_SLAVE_READY   CC26X2R1_LAUNCHXL_SPI_SLAVE_READY

#define Board_UART0             CC26X2R1_LAUNCHXL_UART0
#define Board_UART1             CC26X2R1_LAUNCHXL_UART1

#define Board_WATCHDOG0         CC26X2R1_LAUNCHXL_WATCHDOG0

/* Board specific I2C addresses */
#define Board_TMP_ADDR          (0x40)
#define Board_SENSORS_BP_TMP_ADDR Board_TMP_ADDR

#ifdef __cplusplus
}
#endif

#endif /* __BOARD_H */

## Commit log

2018-09-25 created folder for sponsorship materials plus created documents
2018-10-17 arduino code draft untested
2018-10-17 arduino stream data code untested
2018-11-09 spi stuff
    [adc12_b.obj, aes256.obj, comp_e.obj, crc.obj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]
2018-12-29 entire board first iteration
    [RHD2216_headstage_oldeagle_4.brd, RHD2216_headstage_oldeagle_4.sch]
2019-01-02 modify board, add ref doc, add part lib
    [entireboard_v1.brd, entireboard_v1.sch]
2019-01-03 add jtag connector, crystal, bill of materials; update project lbr
    [BOM.xlsx]
2019-01-03 add connector, crystals, bom, lbr
    [entireboard_v1.brd, entireboard_v1.sch]
2019-01-12 add headers, testpads, current sense resistors, led
    [BOM.xlsx, entireboard_v1.brd, entireboard_v1.sch]
2019-01-12 not sure what happened to autoroute
    [entireboard_v1.brd]
2019-01-14 add CCS projects
    [BIOS.obj, BOM.xlsx, CC26X2R1_LAUNCHXL.obj, CC26X2R1_LAUNCHXL_fxns.obj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]
2019-01-17 board inconsistencies
    [entireboard_v1.brd]
2019-01-18 file organization
    [BIOS.obj, CC26X2R1_LAUNCHXL.obj, CC26X2R1_LAUNCHXL_fxns.obj, ECCROMCC26XX.obj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]
2019-01-18 Update EntireBoard/BOM.xlsx
    added battery stuff to BOM
    [BOM.xlsx]
2019-01-24 2 layer 6x6 cm board
    [entireboard_v2.brd, entireboard_v2.sch]
2019-01-24 BOM quantities updated
    [BOM.xlsx]
2019-01-24 updated BOM quantities
    [BOM.xlsx]
2019-01-24 quantity change to BOM
    [BOM.xlsx]
2019-01-24 BOM changes
    [BOM.xlsx]
2019-01-29 added test LEDs, still 2 layers
    [entireboard_v2.brd]
2019-01-31 4 layer
    [entireboard_v2_4layer.brd, entireboard_v2_4layer.sch]
2019-01-31 widened traces to get 50 ohm impedance matching
    [entireboard_v2_4layer.sch]
2019-02-01 drc for 4-layer
    [entireboard_v2_4layer.brd, entireboard_v2_4layer.sch]
2019-02-01 added more vias to digital side
    [entireboard_v2_4layer.sch]
2019-02-22 add rx/tx
    [smartrf_settings.obj]
2019-02-24 final 4 layer board (with correct regulator)
2019-03-02 modify schematics, changed parts
    [BOM.xlsx, BOM_v2.xlsx, BOM_v3.xlsx, RHD2216_headstage_oldeagle_4.brd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]
2019-03-02 update LED package and JTAG pins
    [BOM_v3.xlsx]
2019-03-07 version 3!! 4x4cm
    [entireboard_v3.sch]
2019-03-11 final (??) board v3
    [BOM_v3.xlsx, entireboard_v3.brd, entireboard_v3.sch]
2019-04-08 showcase poster v1
    [entireboard_v3.brd]
2019-04-27 latest tx code
    [smartrf_settings.obj]
